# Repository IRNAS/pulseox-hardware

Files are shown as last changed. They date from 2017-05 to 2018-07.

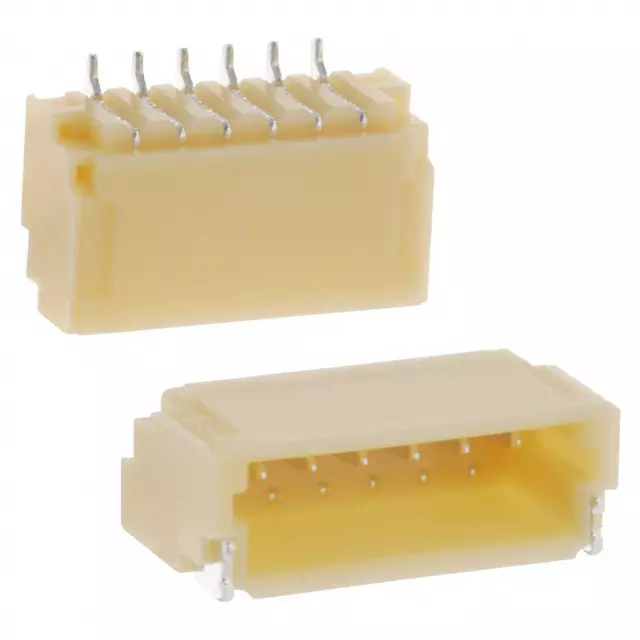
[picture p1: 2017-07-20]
Pics/JST.png

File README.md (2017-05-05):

# pulseox-hardware

---

#### License

All our projects are as usefully open-source as possible.

Hardware including documentation is licensed under [CERN OHL v.1.2. license](http://www.ohwr.org/licenses/cern-ohl/v1.2)

Firmware and software originating from the project is licensed under [GNU GENERAL PUBLIC LICENSE v3](http://www.gnu.org/licenses/gpl-3.0.en.html).

Open data generated by our projects is licensed under [CC0](https://creativecommons.org/publicdomain/zero/1.0/legalcode).

All our websites and additional documentation are licensed under [Creative Commons Attribution-ShareAlike 4 .0 Unported License] (https://creativecommons.org/licenses/by-sa/4.0/legalcode).

What this means is that you can use hardware, firmware, software and documentation without paying a royalty and knowing that you'll be able to use your version forever. You are also free to make changes but if you share these changes then you have to do so on the same conditions that you enjoy.

Koruza, GoodEnoughCNC and IRNAS are all names and marks of Institut IRNAS Rače. 
You may use these names and terms only to attribute the appropriate entity as required by the Open Licences referred to above. You may not use them in any other way and in particular you may not use them to imply endorsement or authorization of any hardware that you design, make or sell.

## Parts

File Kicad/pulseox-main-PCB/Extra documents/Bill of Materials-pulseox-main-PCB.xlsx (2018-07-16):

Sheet: Part List Report
 | Component list |  |  | GliaX - pulseox
 | Source Data From: | pulseox-main-PCB.PrjPcb |  |  | Contact:
 | Project: | pulseox-main-PCB.PrjPcb
 | Variant: | None |  |  |  |  |  |  | IRNAS
 | Report Date: | 02/24/2018 | 8:23:24 PM |  |  |  |  |  | www.irnas.eu
 | Print Date: | 2018-02-24 | 43155.84973
# | Manufacturer Part Number 1 | Manufacturer 1 | Description | Footprint | Designator | Quantity | Supplier 1 | Supplier Part Number 1 | Supplier Order Qty 1 | Supplier Stock 1 | Supplier Unit Price 1 | Supplier Subtotal 1 | Supplier Currency 1
1 | WR08X1002FTL (https://octopart-clicks.com/click/altium?manufacturer=Walsin%20Technologies&mpn=WR08X1002FTL&seller=Farnell&sku=2502671&country=US&channel=BOM%20Report) | Walsin Technologies (https://octopart-clicks.com/click/altium?manufacturer=Walsin%20Technologies&mpn=WR08X1002FTL&seller=Farnell&sku=2502671&country=US&channel=BOM%20Report) | WALSIN - WR08X1002FTL - RES, THICK FILM, 10K, 1%, 150V, 0805 | RES0805 | R4, R6 | 2 | Farnell | 2502671 (https://octopart-clicks.com/click/altium?manufacturer=Walsin%20Technologies&mpn=WR08X1002FTL&seller=Farnell&sku=2502671&country=US&channel=BOM%20Report) | 10 | 43713 | 0.05 | 0.47 | EUR
2 | CRCW08054K70FKEA (https://octopart-clicks.com/click/altium?manufacturer=Vishay&mpn=CRCW08054K70FKEA&seller=Farnell&sku=1469923&country=US&channel=BOM%20Report) | Vishay (https://octopart-clicks.com/click/altium?manufacturer=Vishay&mpn=CRCW08054K70FKEA&seller=Farnell&sku=1469923&country=US&channel=BOM%20Report) | VISHAY - CRCW08054K70FKEA - RES, THICK FILM, 4K7, 1%, 0.125W, 0805 | RES0805 | R3 | 1 | Farnell | 1469923 (https://octopart-clicks.com/click/altium?manufacturer=Vishay&mpn=CRCW08054K70FKEA&seller=Farnell&sku=1469923&country=US&channel=BOM%20Report) | 5 | 3420 |  |  | EUR
3 | WCR0805-47KFI (https://octopart-clicks.com/click/altium?manufacturer=TT%20Welwyn&mpn=WCR0805-47KFI&seller=Farnell&sku=1099812&country=US&channel=BOM%20Report) | TT Welwyn (https://octopart-clicks.com/click/altium?manufacturer=TT%20Welwyn&mpn=WCR0805-47KFI&seller=Farnell&sku=1099812&country=US&channel=BOM%20Report) | WELWYN - WCR0805-47KFI - RES, THICK FILM, 47K, 1%, 0.125W, 0805 | RES0805 | R5 | 1 | Farnell | 1099812 (https://octopart-clicks.com/click/altium?manufacturer=TT%20Welwyn&mpn=WCR0805-47KFI&seller=Farnell&sku=1099812&country=US&channel=BOM%20Report) | 5 | 16160 |  |  | EUR
4 | 1776275-2 (https://octopart-clicks.com/click/altium?manufacturer=TE%20Connectivity&mpn=1776275-2&seller=Farnell&sku=1098611&country=US&channel=BOM%20Report) | TE Connectivity (https://octopart-clicks.com/click/altium?manufacturer=TE%20Connectivity&mpn=1776275-2&seller=Farnell&sku=1098611&country=US&channel=BOM%20Report) | TE CONNECTIVITY - 1776275-2 - TERMINAL BLOCK, WIRE TO BRD, 2POS, 18AWG | Block Terminal 3.5mm | CON2 | 1 | Farnell | 1098611 (https://octopart-clicks.com/click/altium?manufacturer=TE%20Connectivity&mpn=1776275-2&seller=Farnell&sku=1098611&country=US&channel=BOM%20Report) | 5 | 28930 | 0.24 | 1.20 | EUR
5 | CGA4J1X5R1C106K125AC (https://octopart-clicks.com/click/altium?manufacturer=TDK&mpn=CGA4J1X5R1C106K125AC&seller=Farnell&sku=2210948RL&country=US&channel=BOM%20Report) | TDK (https://octopart-clicks.com/click/altium?manufacturer=TDK&mpn=CGA4J1X5R1C106K125AC&seller=Farnell&sku=2210948RL&country=US&channel=BOM%20Report) | TDK - CGA4J1X5R1C106K125AC - CAP, MLCC, X5R, 10UF, 16V, 0805 | CAP0805 | C1 | 1 | Farnell | 2210948RL (https://octopart-clicks.com/click/altium?manufacturer=TDK&mpn=CGA4J1X5R1C106K125AC&seller=Farnell&sku=2210948RL&country=US&channel=BOM%20Report) | 5 | 0 |  |  | EUR
6 | STM32F070F6P6 (https://octopart-clicks.com/click/altium?manufacturer=STMicroelectronics&mpn=STM32F070F6P6&seller=Farnell&sku=2488284&country=US&channel=BOM%20Report) | STMicroelectronics (https://octopart-clicks.com/click/altium?manufacturer=STMicroelectronics&mpn=STM32F070F6P6&seller=Farnell&sku=2488284&country=US&channel=BOM%20Report) | STMICROELECTRONICS STM32F070F6P6 32 Bit Microcontroller, Value Line, ARM Cortex-M0, 48 MHz, 32 KB, 6 KB, 20 Pins, TSSOP | SOP127P600-8N | U3 | 1 | Farnell | 2488284 (https://octopart-clicks.com/click/altium?manufacturer=STMicroelectronics&mpn=STM32F070F6P6&seller=Farnell&sku=2488284&country=US&channel=BOM%20Report) | 5 | 6081 | 2.11 | 10.55 | EUR
7 | AT-2440-TWT-R (https://octopart-clicks.com/click/altium?manufacturer=Projects%20Unlimited&mpn=AT-2440-TWT-R&seller=Digi-Key&sku=668-1103-ND&country=US&channel=BOM%20Report) | Projects Unlimited (https://octopart-clicks.com/click/altium?manufacturer=Projects%20Unlimited&mpn=AT-2440-TWT-R&seller=Digi-Key&sku=668-1103-ND&country=US&channel=BOM%20Report) | AUDIO PIEZO TRANSDUCER 1-30V TH | Buzzer | BUZ1 | 1 | Digi-Key | 668-1103-ND (https://octopart-clicks.com/click/altium?manufacturer=Projects%20Unlimited&mpn=AT-2440-TWT-R&seller=Digi-Key&sku=668-1103-ND&country=US&channel=BOM%20Report) | 5 | 3084 | 1.87 | 9.35 | USD
8 | PS000036 (https://octopart-clicks.com/click/altium?manufacturer=Pro%20Signal&mpn=PS000036&seller=Farnell&sku=2787075&country=US&channel=BOM%20Report) | Pro Signal (https://octopart-clicks.com/click/altium?manufacturer=Pro%20Signal&mpn=PS000036&seller=Farnell&sku=2787075&country=US&channel=BOM%20Report) |  | eth con | CON3 | 1 | Farnell | 2787075 (https://octopart-clicks.com/click/altium?manufacturer=Pro%20Signal&mpn=PS000036&seller=Farnell&sku=2787075&country=US&channel=BOM%20Report) |  | 0 |  |  | Loading...
9 | NX7002BK (https://octopart-clicks.com/click/altium?manufacturer=NXP%20Semiconductors&mpn=NX7002BK&seller=Farnell&sku=2469640&country=US&channel=BOM%20Report) | NXP Semiconductors (https://octopart-clicks.com/click/altium?manufacturer=NXP%20Semiconductors&mpn=NX7002BK&seller=Farnell&sku=2469640&country=US&channel=BOM%20Report) | NEXPERIA - NX7002BK - MOSFET, N-CH, 60V, 0.27A, SOT-23-3 | SOT23 | T1 | 1 | Farnell | 2469640 (https://octopart-clicks.com/click/altium?manufacturer=NXP%20Semiconductors&mpn=NX7002BK&seller=Farnell&sku=2469640&country=US&channel=BOM%20Report) | 5 | 175 | 0.26 | 1.29 | EUR
10 | GRM219R71C104KA01D (https://octopart-clicks.com/click/altium?manufacturer=Murata&mpn=GRM219R71C104KA01D&seller=Farnell&sku=2611934&country=US&channel=BOM%20Report) | Murata (https://octopart-clicks.com/click/altium?manufacturer=Murata&mpn=GRM219R71C104KA01D&seller=Farnell&sku=2611934&country=US&channel=BOM%20Report) | MURATA - GRM219R71C104KA01D - CAP, MLCC, X7R, 0.1UF, 16V, 0805 | CAP0805 | C2, C16 | 2 | Farnell | 2611934 (https://octopart-clicks.com/click/altium?manufacturer=Murata&mpn=GRM219R71C104KA01D&seller=Farnell&sku=2611934&country=US&channel=BOM%20Report) | 10 | 4457 | 0.10 | 0.98 | EUR
11 | GRM21BR71C105KA01K (https://octopart-clicks.com/click/altium?manufacturer=Murata&mpn=GRM21BR71C105KA01K&seller=Farnell&sku=2688536&country=US&channel=BOM%20Report) | Murata (https://octopart-clicks.com/click/altium?manufacturer=Murata&mpn=GRM21BR71C105KA01K&seller=Farnell&sku=2688536&country=US&channel=BOM%20Report) | MURATA - GRM21BR71C105KA01K - CAP, MLCC, X7R, 1UF, 16V, 0805 | CAP0805 | C3, C4 | 2 | Farnell | 2688536 (https://octopart-clicks.com/click/altium?manufacturer=Murata&mpn=GRM21BR71C105KA01K&seller=Farnell&sku=2688536&country=US&channel=BOM%20Report) | 10 | 15026 | 0.10 | 1.03 | EUR
12 | MCWR08X1002FTL (https://octopart-clicks.com/click/altium?manufacturer=Multicomp&mpn=MCWR08X1002FTL&seller=Farnell&sku=2446870&country=US&channel=BOM%20Report) | Multicomp (https://octopart-clicks.com/click/altium?manufacturer=Multicomp&mpn=MCWR08X1002FTL&seller=Farnell&sku=2446870&country=US&channel=BOM%20Report) | MULTICOMP MCWR08X1002FTL Surface Mount Chip Resistor, Thick Film, MCWR Series, 10 kohm, 125 mW, 1%, 150 V | RES0805 | R7 | 1 | Farnell | 2446870 (https://octopart-clicks.com/click/altium?manufacturer=Multicomp&mpn=MCWR08X1002FTL&seller=Farnell&sku=2446870&country=US&channel=BOM%20Report) | 5 | 2650000 |  |  | EUR
13 | MCMR06X102JTL (https://octopart-clicks.com/click/altium?manufacturer=Multicomp&mpn=MCMR06X102JTL&seller=Farnell&sku=2073354&country=US&channel=BOM%20Report) | Multicomp (https://octopart-clicks.com/click/altium?manufacturer=Multicomp&mpn=MCMR06X102JTL&seller=Farnell&sku=2073354&country=US&channel=BOM%20Report) | MULTICOMP - MCMR06X102 JTL - RES, CERAMIC, 1K, 5%, 0.1W, 0603 | RES0603 | R2 | 1 | Farnell | 2073354 (https://octopart-clicks.com/click/altium?manufacturer=Multicomp&mpn=MCMR06X102JTL&seller=Farnell&sku=2073354&country=US&channel=BOM%20Report) | 5 | 11690 |  |  | EUR
14 | MCMR06X103JTL (https://octopart-clicks.com/click/altium?manufacturer=Multicomp&mpn=MCMR06X103JTL&seller=Farnell&sku=2073356&country=US&channel=BOM%20Report) | Multicomp (https://octopart-clicks.com/click/altium?manufacturer=Multicomp&mpn=MCMR06X103JTL&seller=Farnell&sku=2073356&country=US&channel=BOM%20Report) | MULTICOMP - MCMR06X103 JTL - RES, CERAMIC, 10K, 5%, 0.1W, 0603 | RES0603 | R1 | 1 | Farnell | 2073356 (https://octopart-clicks.com/click/altium?manufacturer=Multicomp&mpn=MCMR06X103JTL&seller=Farnell&sku=2073356&country=US&channel=BOM%20Report) | 5 | 11369 |  |  | EUR
15 | MCP1700T-3002E/TT (https://octopart-clicks.com/click/altium?manufacturer=Microchip&mpn=MCP1700T-3002E%2FTT&seller=Farnell&sku=1331482&country=US&channel=BOM%20Report) | Microchip (https://octopart-clicks.com/click/altium?manufacturer=Microchip&mpn=MCP1700T-3002E%2FTT&seller=Farnell&sku=1331482&country=US&channel=BOM%20Report) | MICROCHIP - MCP1700T-3002E/TT - IC, LDO REGULATOR, 0.25A, 6V, SOT23-3 | SOT23127P600-8N - duplicate | U2 | 1 | Farnell | 1331482 (https://octopart-clicks.com/click/altium?manufacturer=Microchip&mpn=MCP1700T-3002E%2FTT&seller=Farnell&sku=1331482&country=US&channel=BOM%20Report) | 5 | 25139 | 0.34 | 1.70 | EUR
16 | MCP73831T-2ACI/OT (https://octopart-clicks.com/click/altium?manufacturer=Microchip&mpn=MCP73831T-2ACI%2FOT&seller=Farnell&sku=1332158&country=US&channel=BOM%20Report) | Microchip (https://octopart-clicks.com/click/altium?manufacturer=Microchip&mpn=MCP73831T-2ACI%2FOT&seller=Farnell&sku=1332158&country=US&channel=BOM%20Report) | MICROCHIP - MCP73831T-2ACI/OT - LI-ION/LI-POLY CHARGE CONTROLLER | SOT23127P600-8N | U1 | 1 | Farnell | 1332158 (https://octopart-clicks.com/click/altium?manufacturer=Microchip&mpn=MCP73831T-2ACI%2FOT&seller=Farnell&sku=1332158&country=US&channel=BOM%20Report) | 5 | 41449 | 0.52 | 2.60 | EUR
17 | Loading... (https://octopart-clicks.com/click/altium?manufacturer=Loading...&mpn=Loading...&seller=Farnell&sku=1813692&country=US&channel=BOM%20Report) | Loading... (https://octopart-clicks.com/click/altium?manufacturer=Loading...&mpn=Loading...&seller=Farnell&sku=1813692&country=US&channel=BOM%20Report) | TE CONNECTIVITY FSMRA4JH04 Tactile Switch, Non Illuminated, 1.57 N, 24 V, 50 mA, Solder, FSMRAJ Series | SW TH ANGLE_1 | SW4 | 1 | Farnell | 1813692 (https://octopart-clicks.com/click/altium?manufacturer=Loading...&mpn=Loading...&seller=Farnell&sku=1813692&country=US&channel=BOM%20Report) |  |  |  |  | Loading...
18 | OS102011MA1QS1 (https://octopart-clicks.com/click/altium?manufacturer=ITT%20C%26K&mpn=OS102011MA1QS1&seller=Farnell&sku=2435103&country=US&channel=BOM%20Report) | ITT C&K (https://octopart-clicks.com/click/altium?manufacturer=ITT%20C%26K&mpn=OS102011MA1QS1&seller=Farnell&sku=2435103&country=US&channel=BOM%20Report) | C & K COMPONENTS - OS102011MA1QS1 - SWITCH SLIDE SHORTING SPDT | SLIDE_SW | SW1 | 1 | Farnell | 2435103 (https://octopart-clicks.com/click/altium?manufacturer=ITT%20C%26K&mpn=OS102011MA1QS1&seller=Farnell&sku=2435103&country=US&channel=BOM%20Report) | 5 | 1441 | 0.25 | 1.25 | EUR
19 | PTS645VH58-2LFS (https://octopart-clicks.com/click/altium?manufacturer=ITT%20C%26K&mpn=PTS645VH58-2LFS&seller=Farnell&sku=2320088&country=US&channel=BOM%20Report) | ITT C&K (https://octopart-clicks.com/click/altium?manufacturer=ITT%20C%26K&mpn=PTS645VH58-2LFS&seller=Farnell&sku=2320088&country=US&channel=BOM%20Report) | SWITCH TACTILE SPST-NO 0.05A 12V | SW TH ANGLE_2 | SW2 | 1 | Farnell | 2320088 (https://octopart-clicks.com/click/altium?manufacturer=ITT%20C%26K&mpn=PTS645VH58-2LFS&seller=Farnell&sku=2320088&country=US&channel=BOM%20Report) | 5 | 7080 | 0.19 | 0.94 | GBP
20 | HSMS-C190 (https://octopart-clicks.com/click/altium?manufacturer=Broadcom%20Avago&mpn=HSMS-C190&seller=Farnell&sku=2497356&country=US&channel=BOM%20Report) | Broadcom Avago (https://octopart-clicks.com/click/altium?manufacturer=Broadcom%20Avago&mpn=HSMS-C190&seller=Farnell&sku=2497356&country=US&channel=BOM%20Report) | BROADCOM LIMITED - HSMS-C190 - LED, RED, 10MCD, 626NM | LED0603 | D1 | 1 | Farnell | 2497356 (https://octopart-clicks.com/click/altium?manufacturer=Broadcom%20Avago&mpn=HSMS-C190&seller=Farnell&sku=2497356&country=US&channel=BOM%20Report) |  | 11495 |  |  | Loading...
21 |  |  |  | microUSB-CHINA | CON1 | 1
22 |  |  | Header, 4-Pin | HDR1X4 | P1 | 1
23 |  |  | Header, 8-Pin | HDR1X8 | P2 | 1
 |  |  |  |  |  | 26 |  |  | 100 |  |  | 31.366
Approved |  |  |  | Notes
 |  |  |  | pcs: |  | 5 |  | Total |  | 31.366 |  | <none>
 |  |  |  |  |  |  |  | Price for 1pcs |  | 6.27 |  | <none>

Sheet: Project Information
Project Full Path | C:\Users\vojislav\Documents\Projects\pulseox-hardware\pulseox-main-PCB\pulseox-main-PCB.PrjPcb
Project Filename | pulseox-main-PCB.PrjPcb
Variant Name | None
Data-Source Filename | pulseox-main-PCB.PrjPcb
Data-Source Full Path | C:\Users\vojislav\Documents\Projects\pulseox-hardware\pulseox-main-PCB\pulseox-main-PCB.PrjPcb
Title | <Parameter Title not found>
Total Quantity | 26
Report Time | 8:23:24 PM
Report Date | 02/24/2018
Report Date & Tine | 02/24/2018 8:23:24 PM
Output Name | Bill of Materials
Output Type | BOM_PartType
Output Generator Name | BOM
Output Generator Description | Bill of Materials

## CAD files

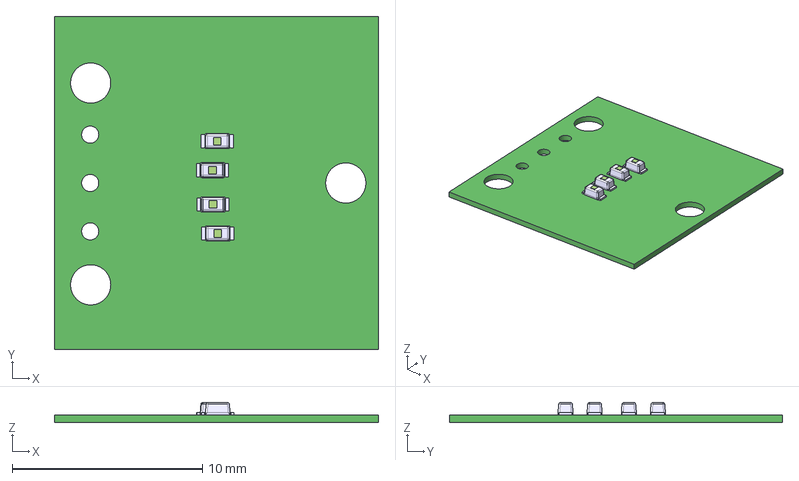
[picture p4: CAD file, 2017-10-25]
PCB_step_files/pulseox-clamp-PCB_diode_v2_0.step
17.0 x 17.5 x 1.07 mm
Board
LED_SMD_0603 x 4
Extruded x 4

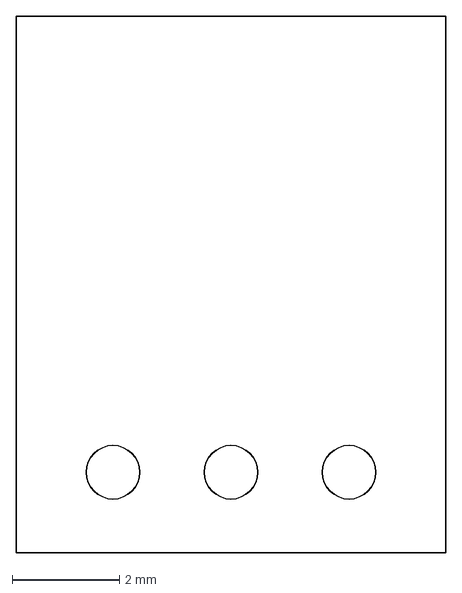
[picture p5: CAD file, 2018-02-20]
pulseox-clamp-led-PCB/pcb_test.dxf
8.00 x 10.0 mm

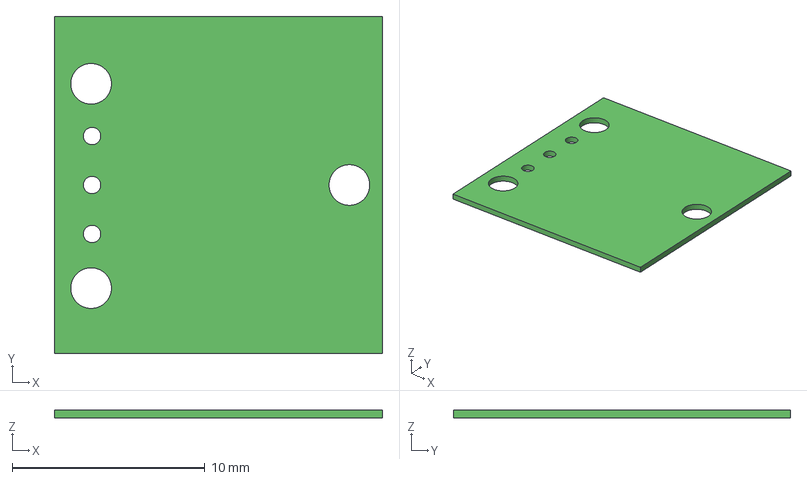
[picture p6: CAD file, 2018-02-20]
pulseox-clamp-PCB/pulseox-clamp-PCB_v2_0.step
17.0 x 17.5 x 0.411 mm

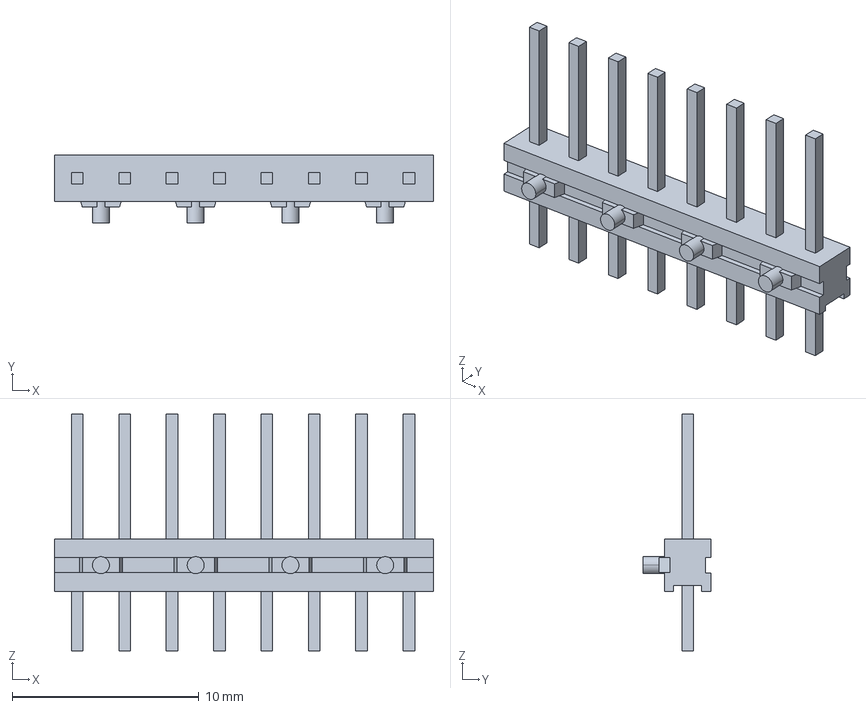
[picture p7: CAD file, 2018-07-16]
pulseox-main-PCB/step/header8pin.stp
20.3 x 3.65 x 12.7 mm

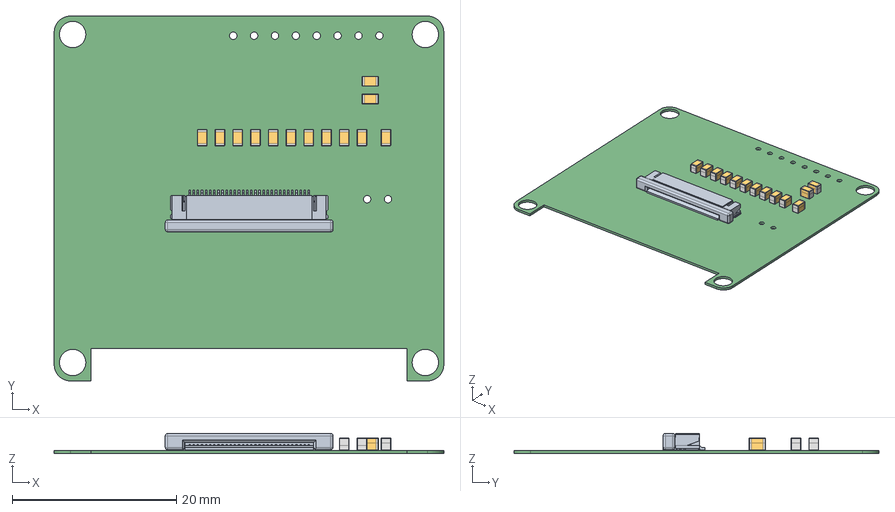
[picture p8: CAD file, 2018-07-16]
pulseox_brakeout_LCD_PCB/pulseox_brakeout_LCD_PCB.step
47.4 x 44.4 x 2.47 mm
Board
c-3-1734592-0-c-3d
CAPC2012X95N_EIA_0805 x 26

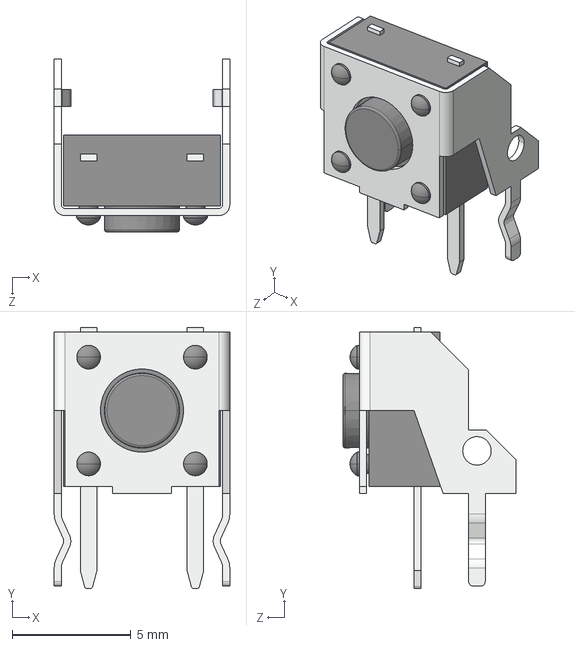
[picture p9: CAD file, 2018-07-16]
pulseox-main-PCB/step/User Library-SWITCH, TACTILE, RIGHT ANGLE, 12VDC, 50MA, 3_15MM ACTUATOR, WEALTH METAL TC-0240Z.step
7.40 x 11.0 x 7.30 mm

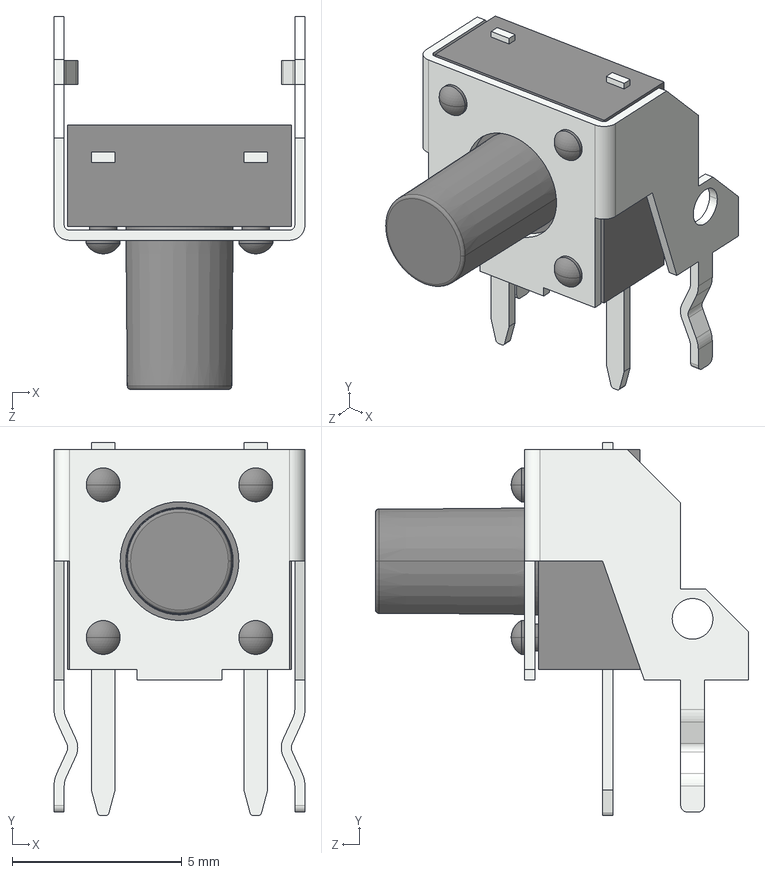
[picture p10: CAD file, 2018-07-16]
pulseox-main-PCB/step/User Library-SWITCH, TACTILE, RIGHT ANGLE, 12VDC, 50MA, 6_85MM ACTUATOR, WEALTH METAL TC-0244Z.step
7.40 x 11.0 x 11.0 mm

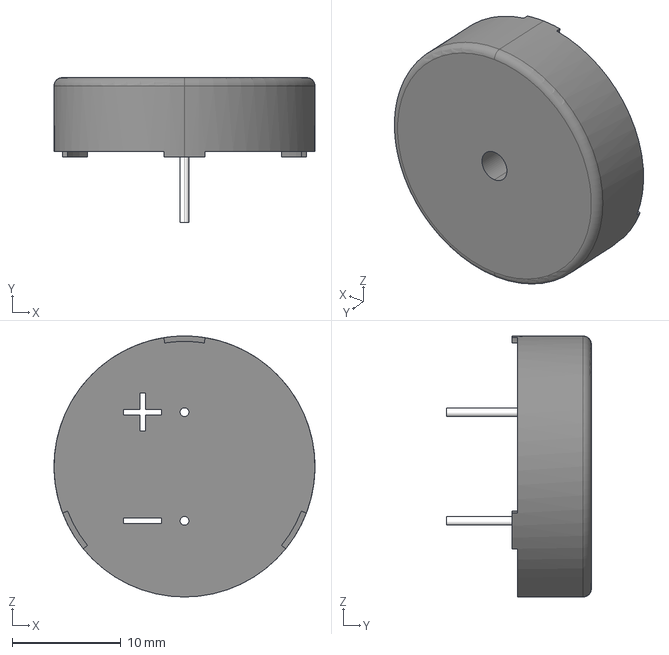
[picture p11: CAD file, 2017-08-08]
pulseox-main-PCB/step/buzz.stp
24.0 x 13.3 x 24.0 mm

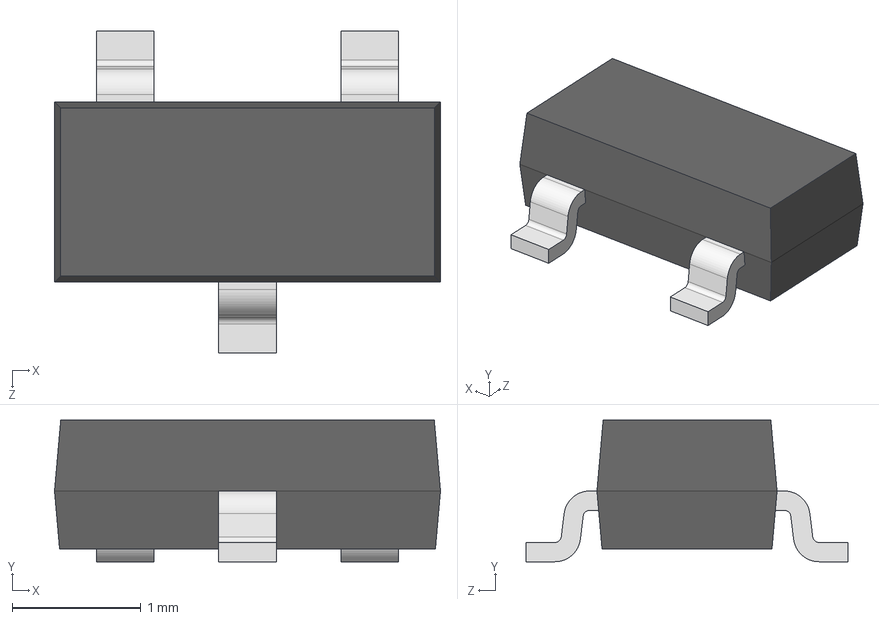
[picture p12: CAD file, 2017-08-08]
pulseox-main-PCB/step/SOT-23.step
3.00 x 1.10 x 2.50 mm

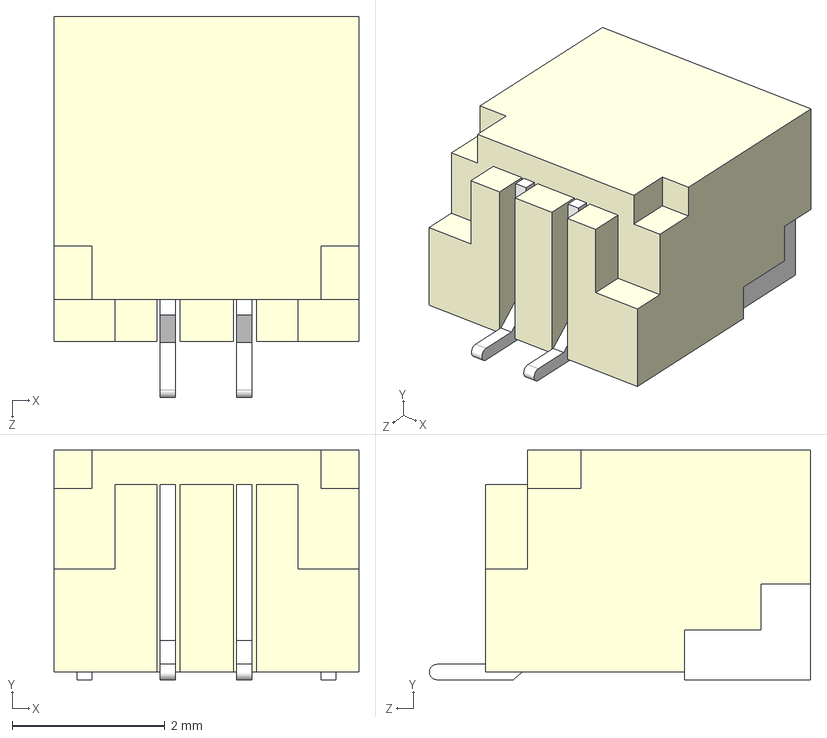
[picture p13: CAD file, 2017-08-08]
pulseox-main-PCB/step/JST_SM02B-SRSS-TB.step
3.99 x 3.00 x 4.99 mm

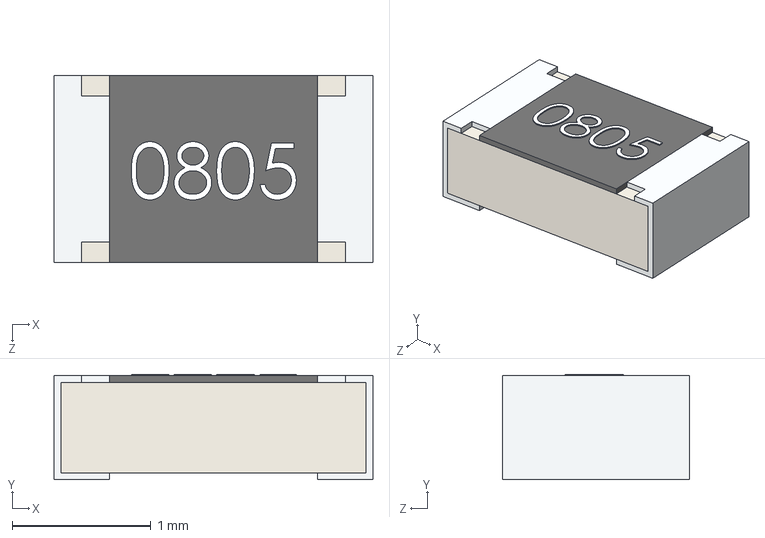
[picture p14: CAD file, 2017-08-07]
pulseox-main-PCB/step/RES-0805.step
2.30 x 0.76 x 1.35 mm

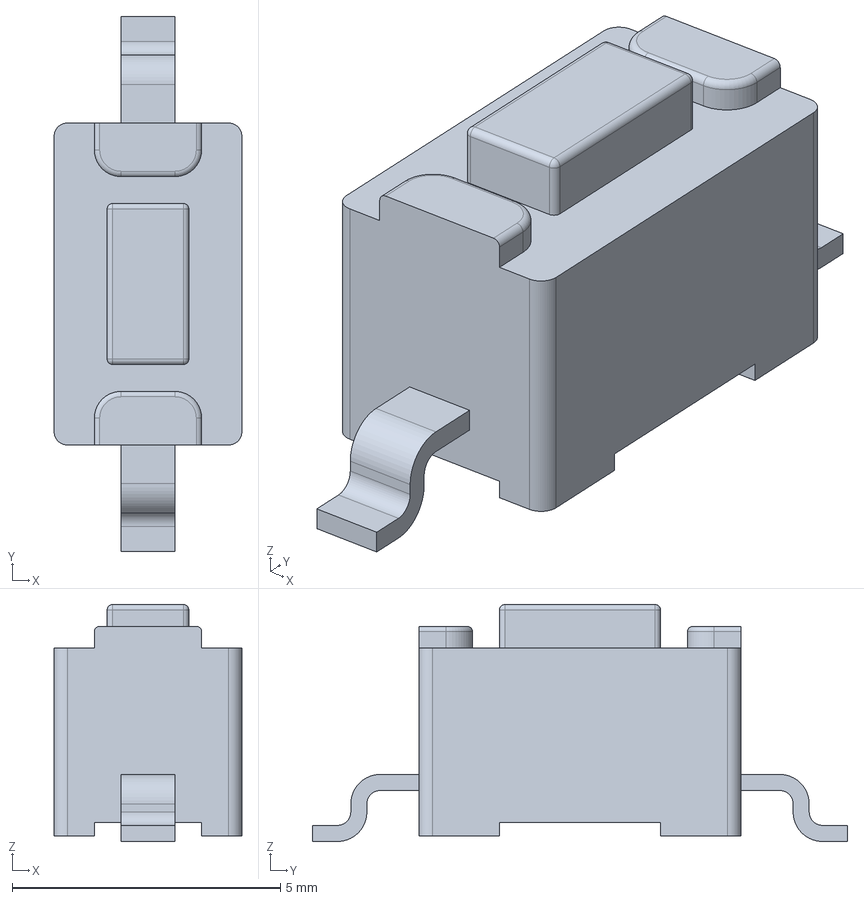
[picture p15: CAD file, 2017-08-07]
pulseox-main-PCB/step/fsmsm.stp
3.50 x 9.97 x 4.42 mm

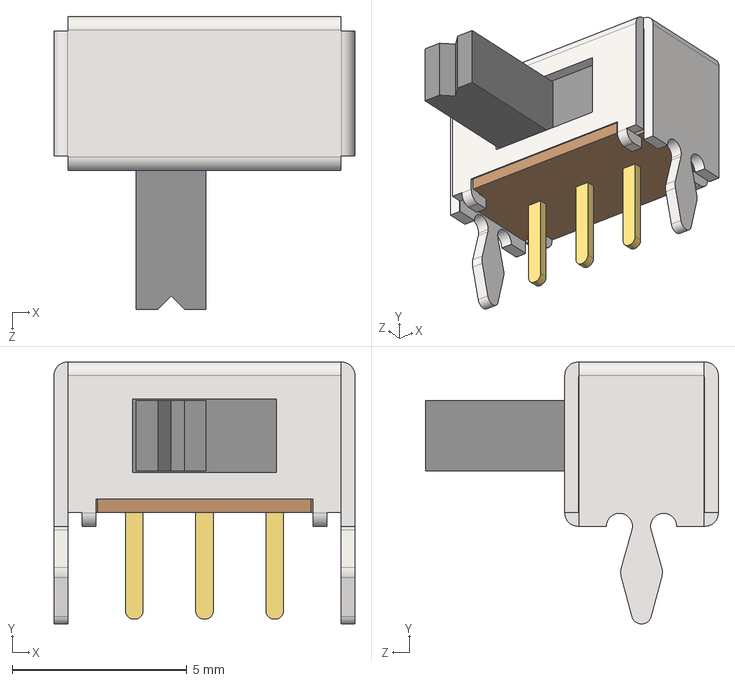
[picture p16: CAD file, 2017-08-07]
pulseox-main-PCB/step/CK_Slide.step
8.61 x 7.49 x 8.37 mm

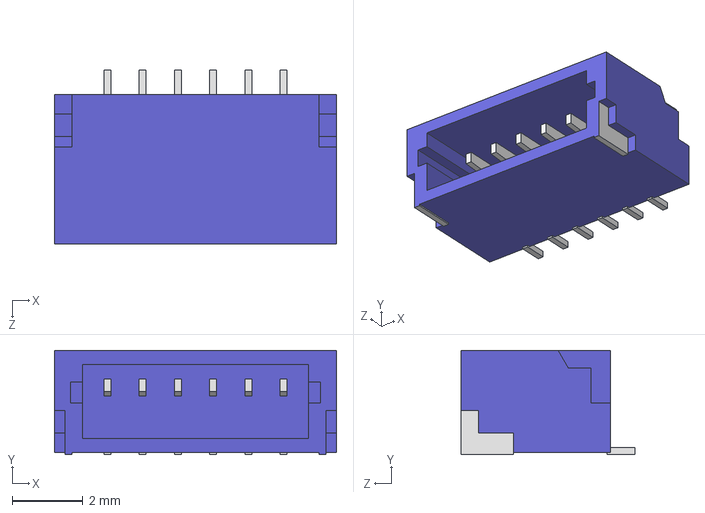
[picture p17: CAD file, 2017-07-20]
pulseox-main-PCB/step/SM06B-SRSS-TB.STEP
8.00 x 2.96 x 4.95 mm

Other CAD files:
PCB_step_files/pulseox-clamp-PCB_v2_0.step
pulseox-clamp-led-PCB/pulseox-clamp-PCB_diode_v2_0.step
pulseox-main-PCB/step/SHR-06V-S-B.STEP
pulseox-main-PCB/step/SHR-06V-S.STEP

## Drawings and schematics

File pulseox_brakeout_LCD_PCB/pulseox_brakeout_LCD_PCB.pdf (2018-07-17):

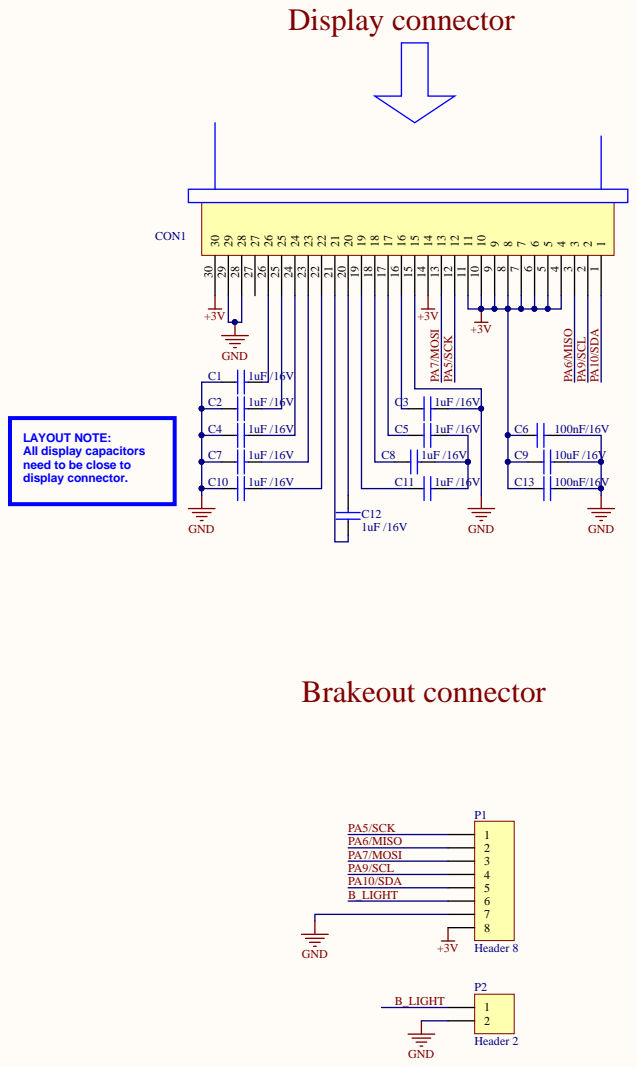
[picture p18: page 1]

LAYOUT NOTE:
All display capacitors
need to be close to
display connector.

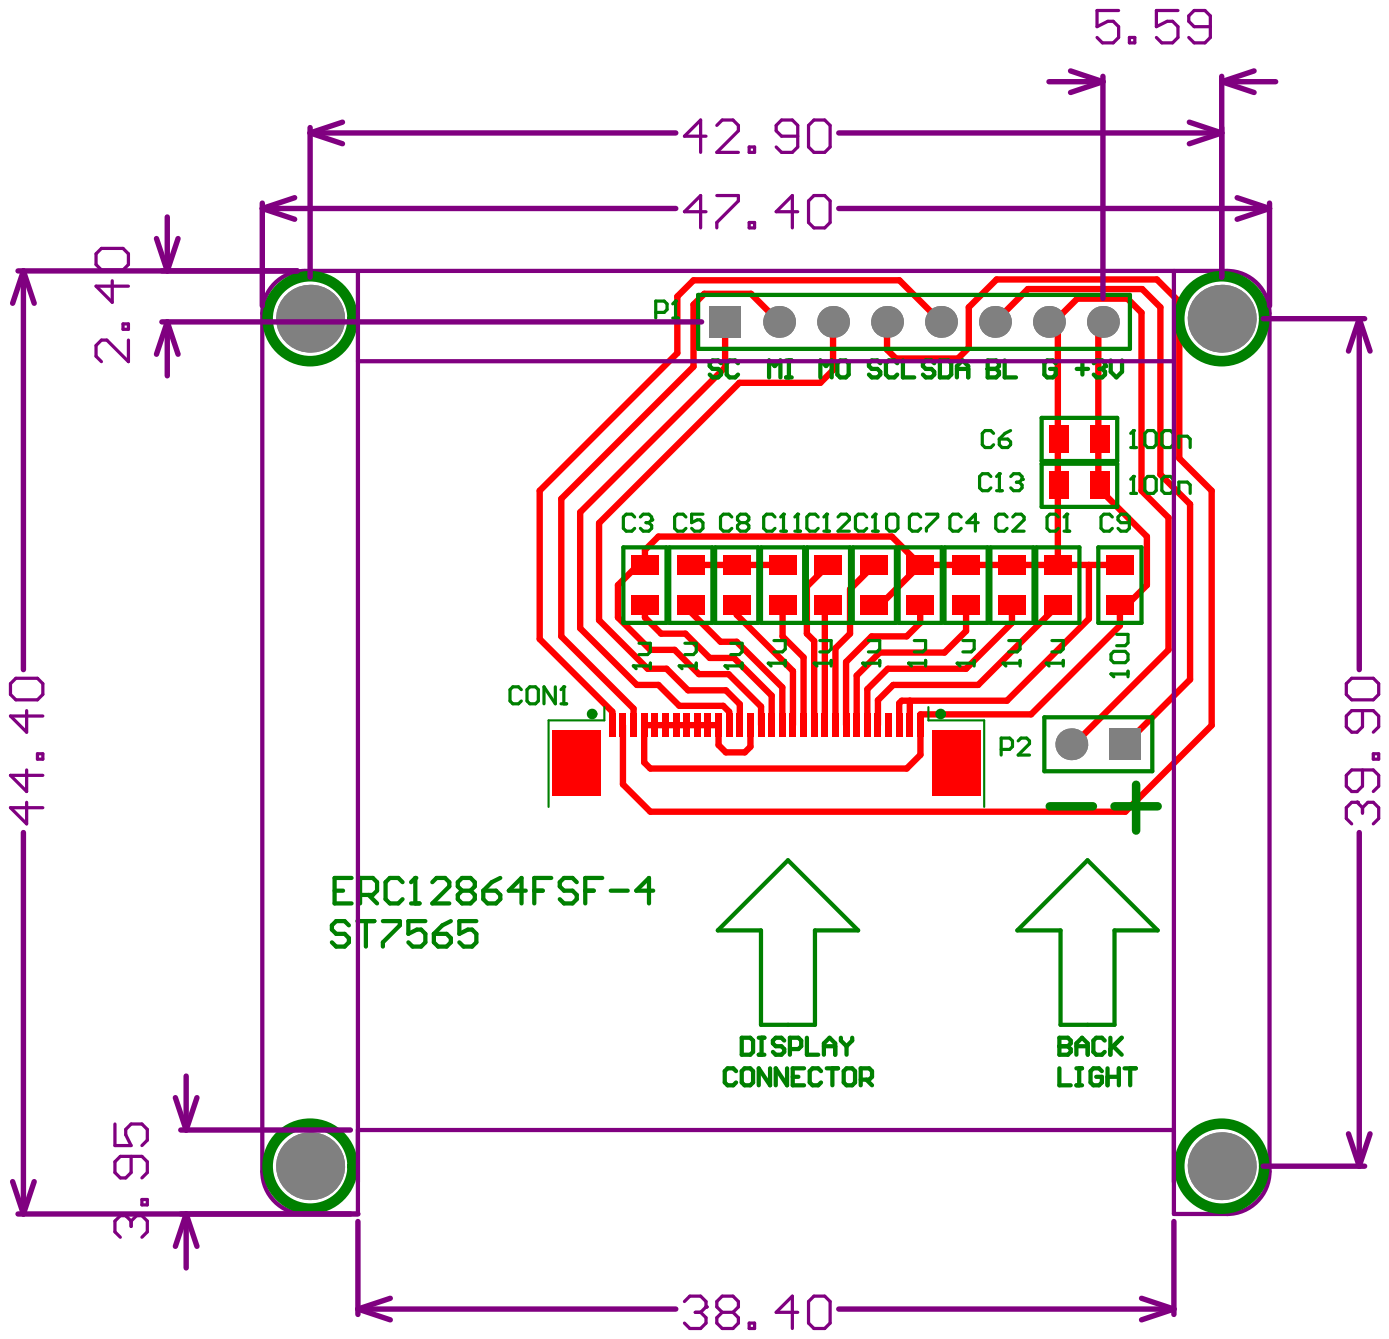
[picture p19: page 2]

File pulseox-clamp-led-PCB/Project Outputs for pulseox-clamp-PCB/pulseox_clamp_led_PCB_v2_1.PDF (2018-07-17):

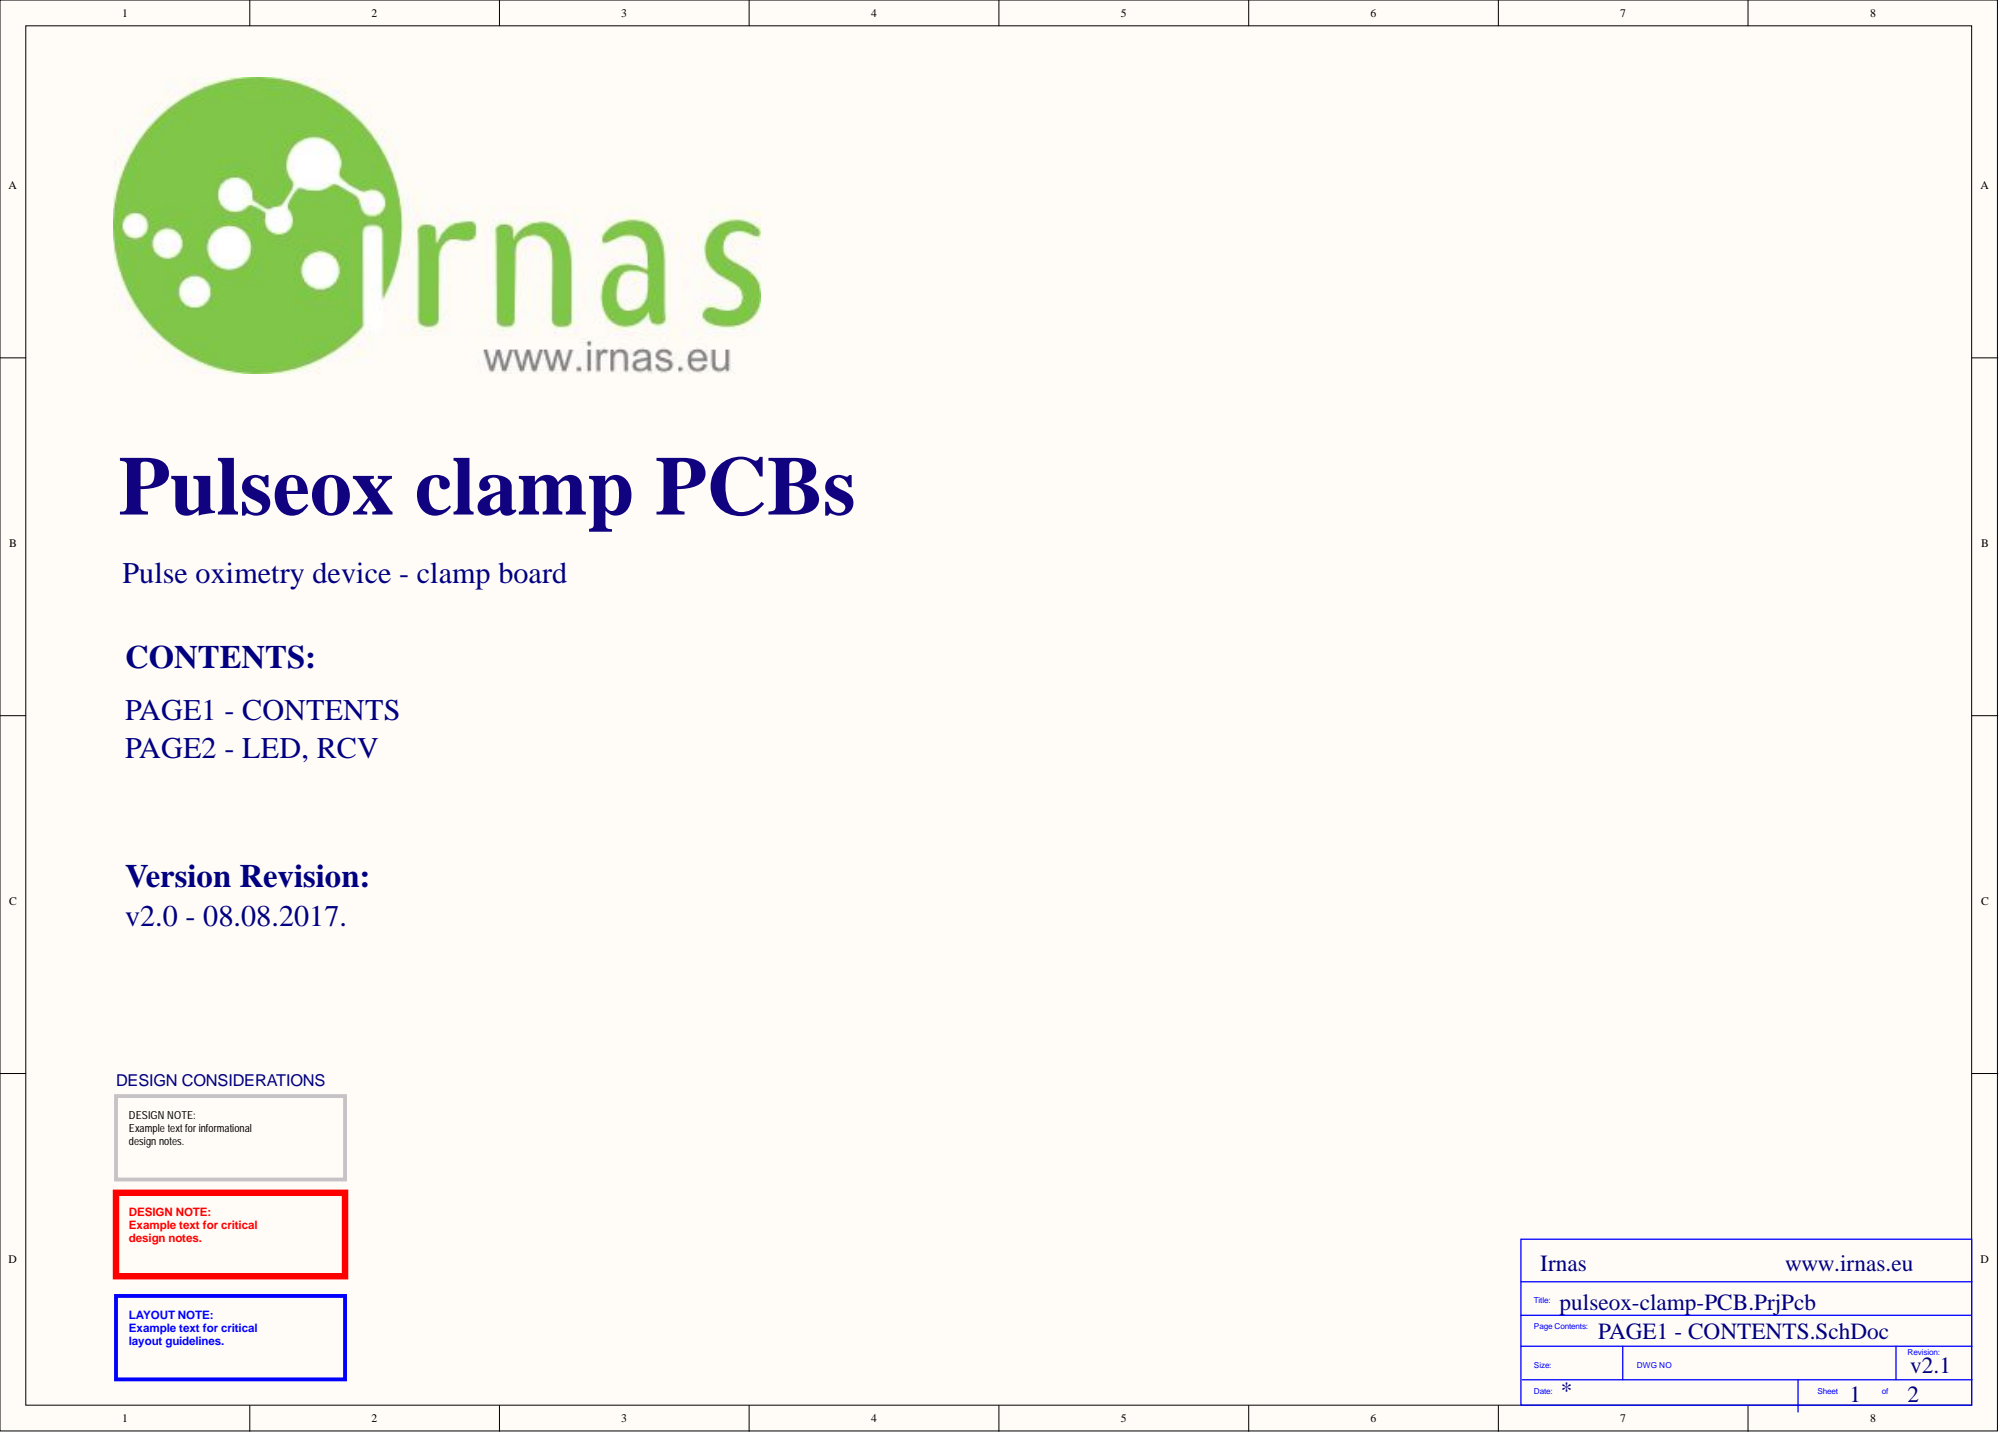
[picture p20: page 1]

Pulse oximetry device - clamp board

DESIGN NOTE:
Example text for informational
design notes.

Example text for critical

pulseox-clamp-PCB.PrjPcb
PAGE1 - CONTENTS.SchDoc

LAYOUT NOTE:
layout guidelines.

Size: | DWG NO | Revision: v2.1

* Date: | 1 2 Sheet of

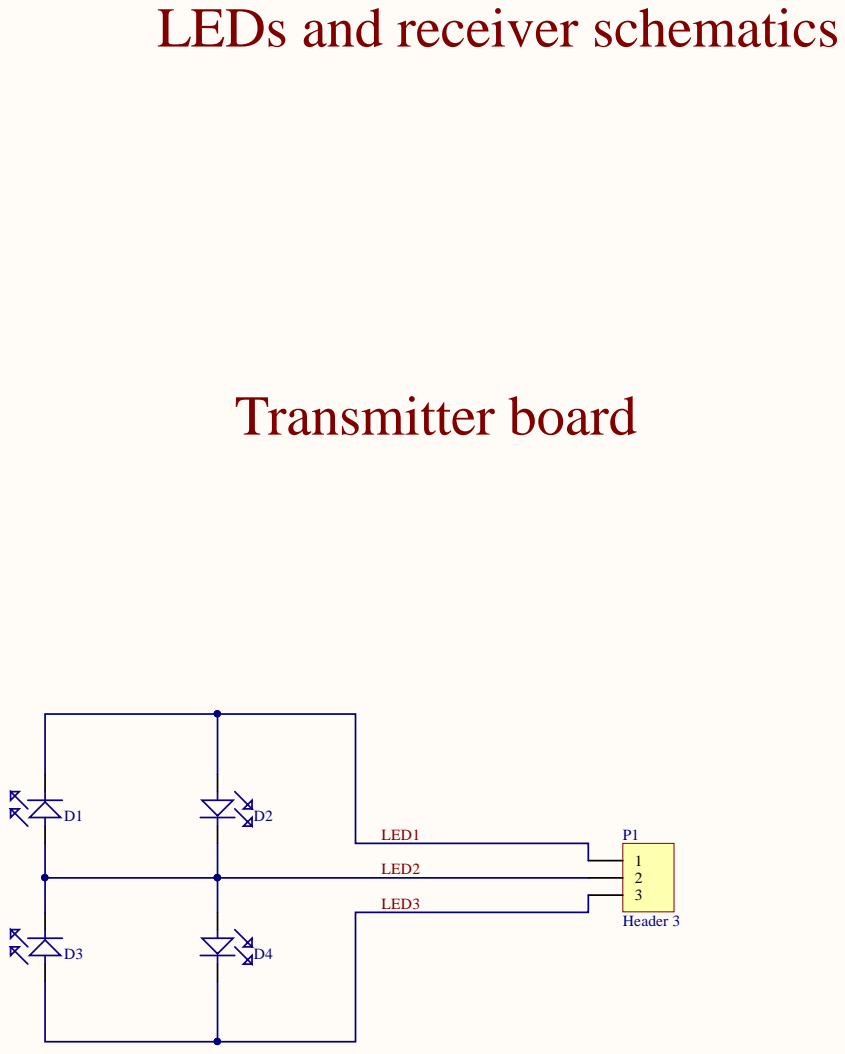
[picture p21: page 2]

LEDs and receiver schematics Transmitter board123

S i z e : | DWG N O | R e v i s i o n : v2.1

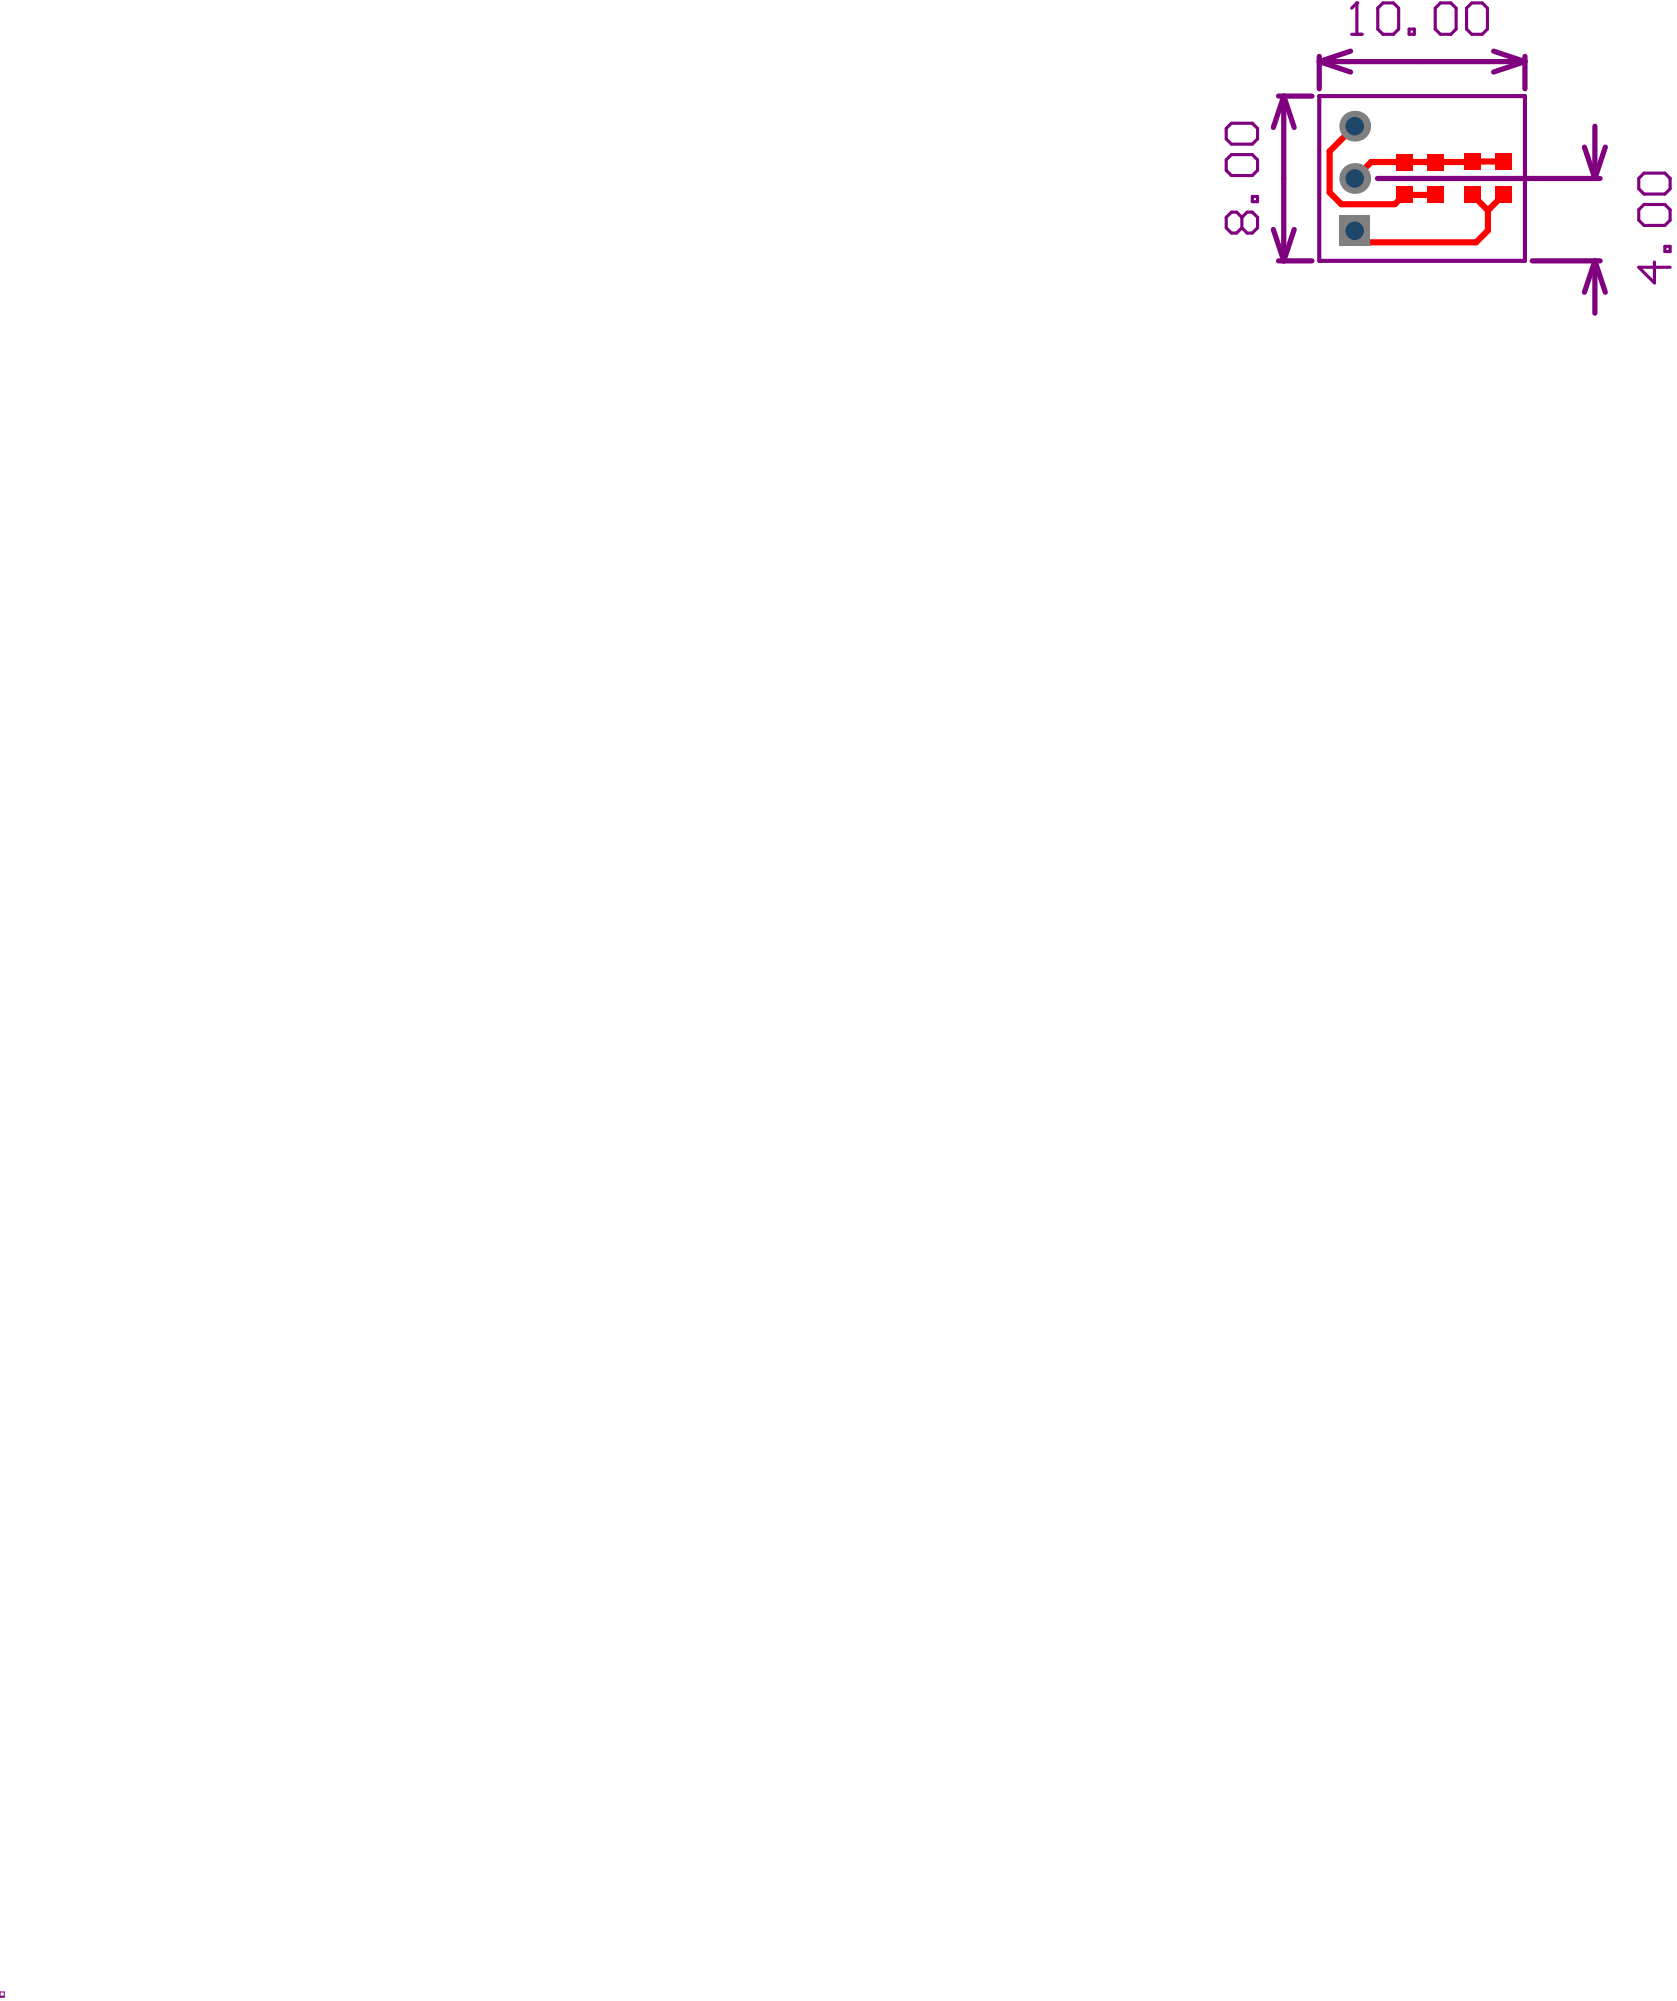
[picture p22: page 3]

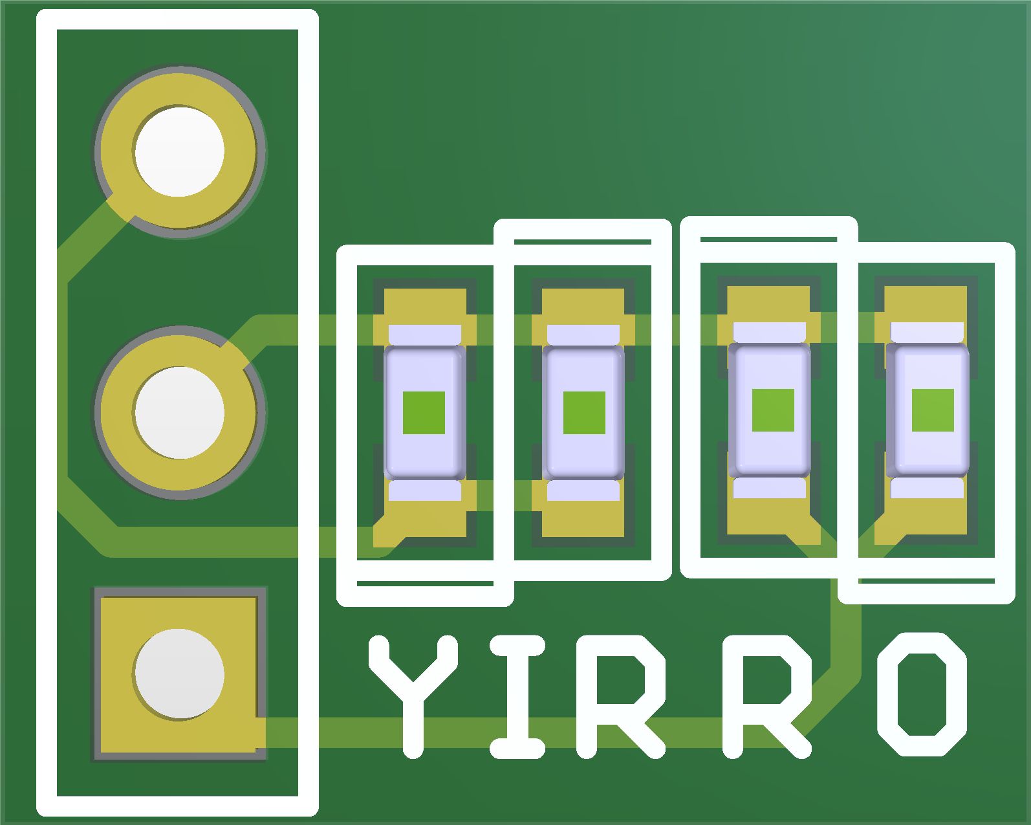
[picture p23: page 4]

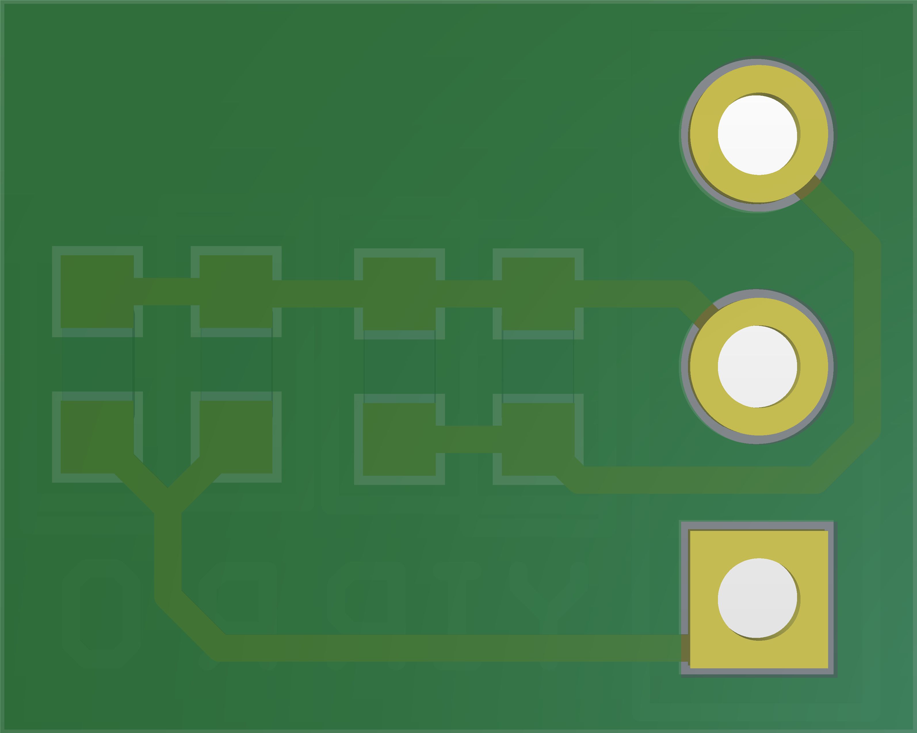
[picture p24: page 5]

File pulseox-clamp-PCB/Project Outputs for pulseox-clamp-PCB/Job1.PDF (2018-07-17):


Pulse oximetry device - clamp board

DESIGN NOTE:
Example text for informational
design notes.

Example text for critical

pulseox-clamp-PCB.PrjPcb
PAGE1 - CONTENTS.SchDoc

LAYOUT NOTE:
layout guidelines.

Size: | DWG NO | Revision: v2.1

* Date: | 1 2 Sheet of

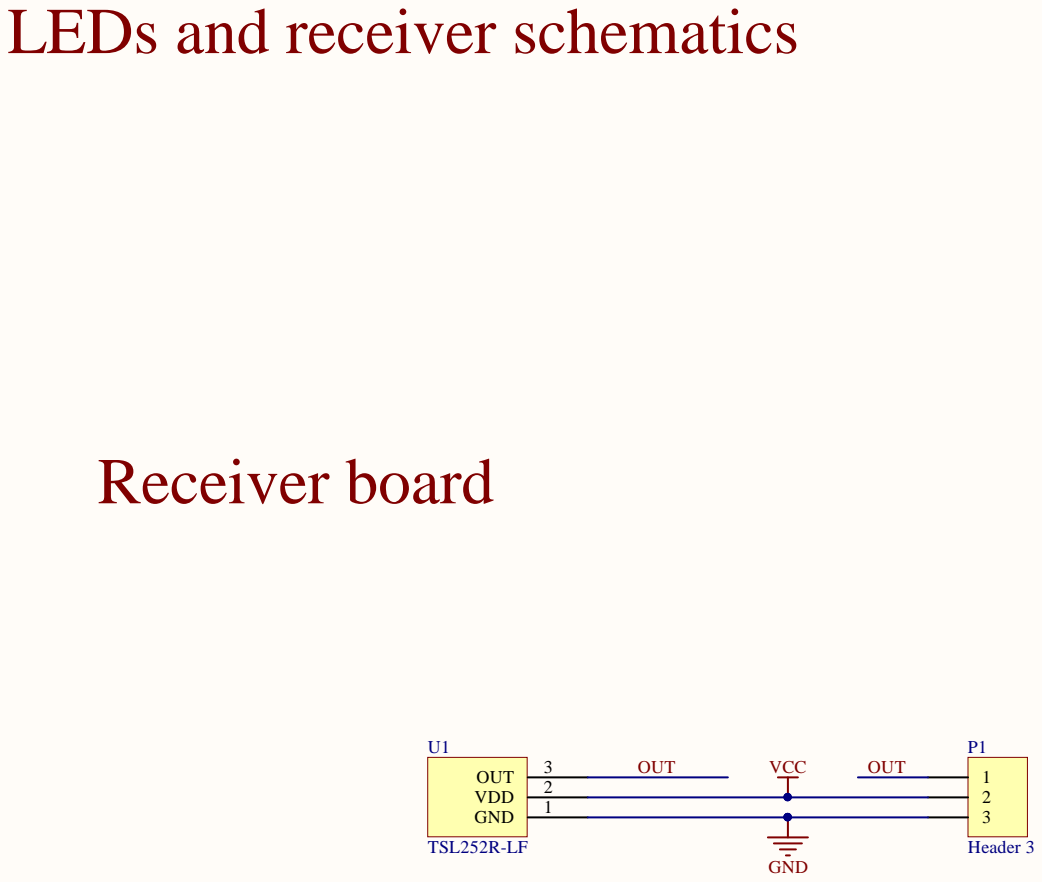
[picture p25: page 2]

LEDs and receiver schematics

S i z e : | DWG N O | R e v i s i o n : v2.1

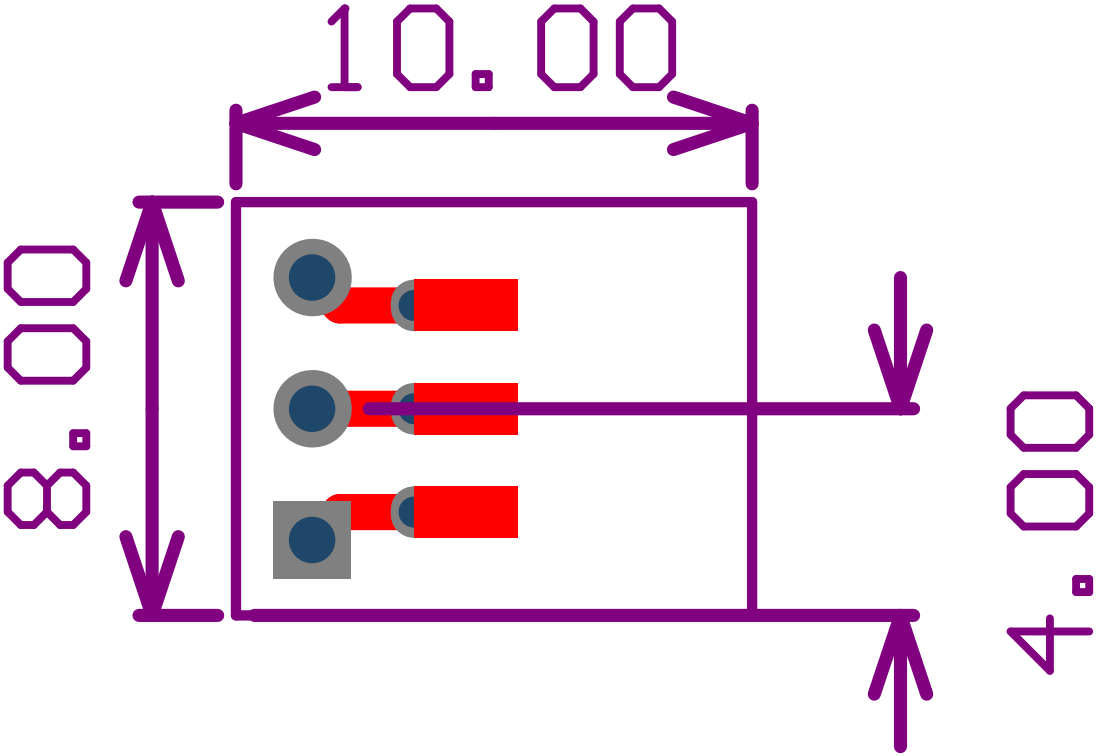
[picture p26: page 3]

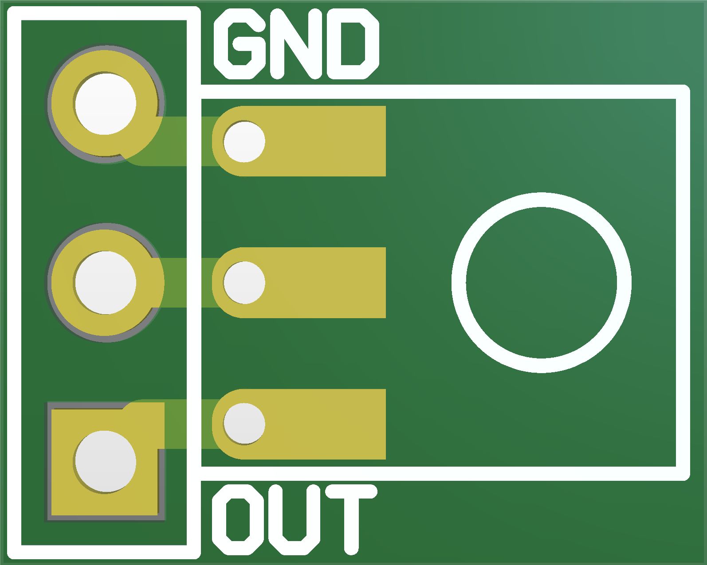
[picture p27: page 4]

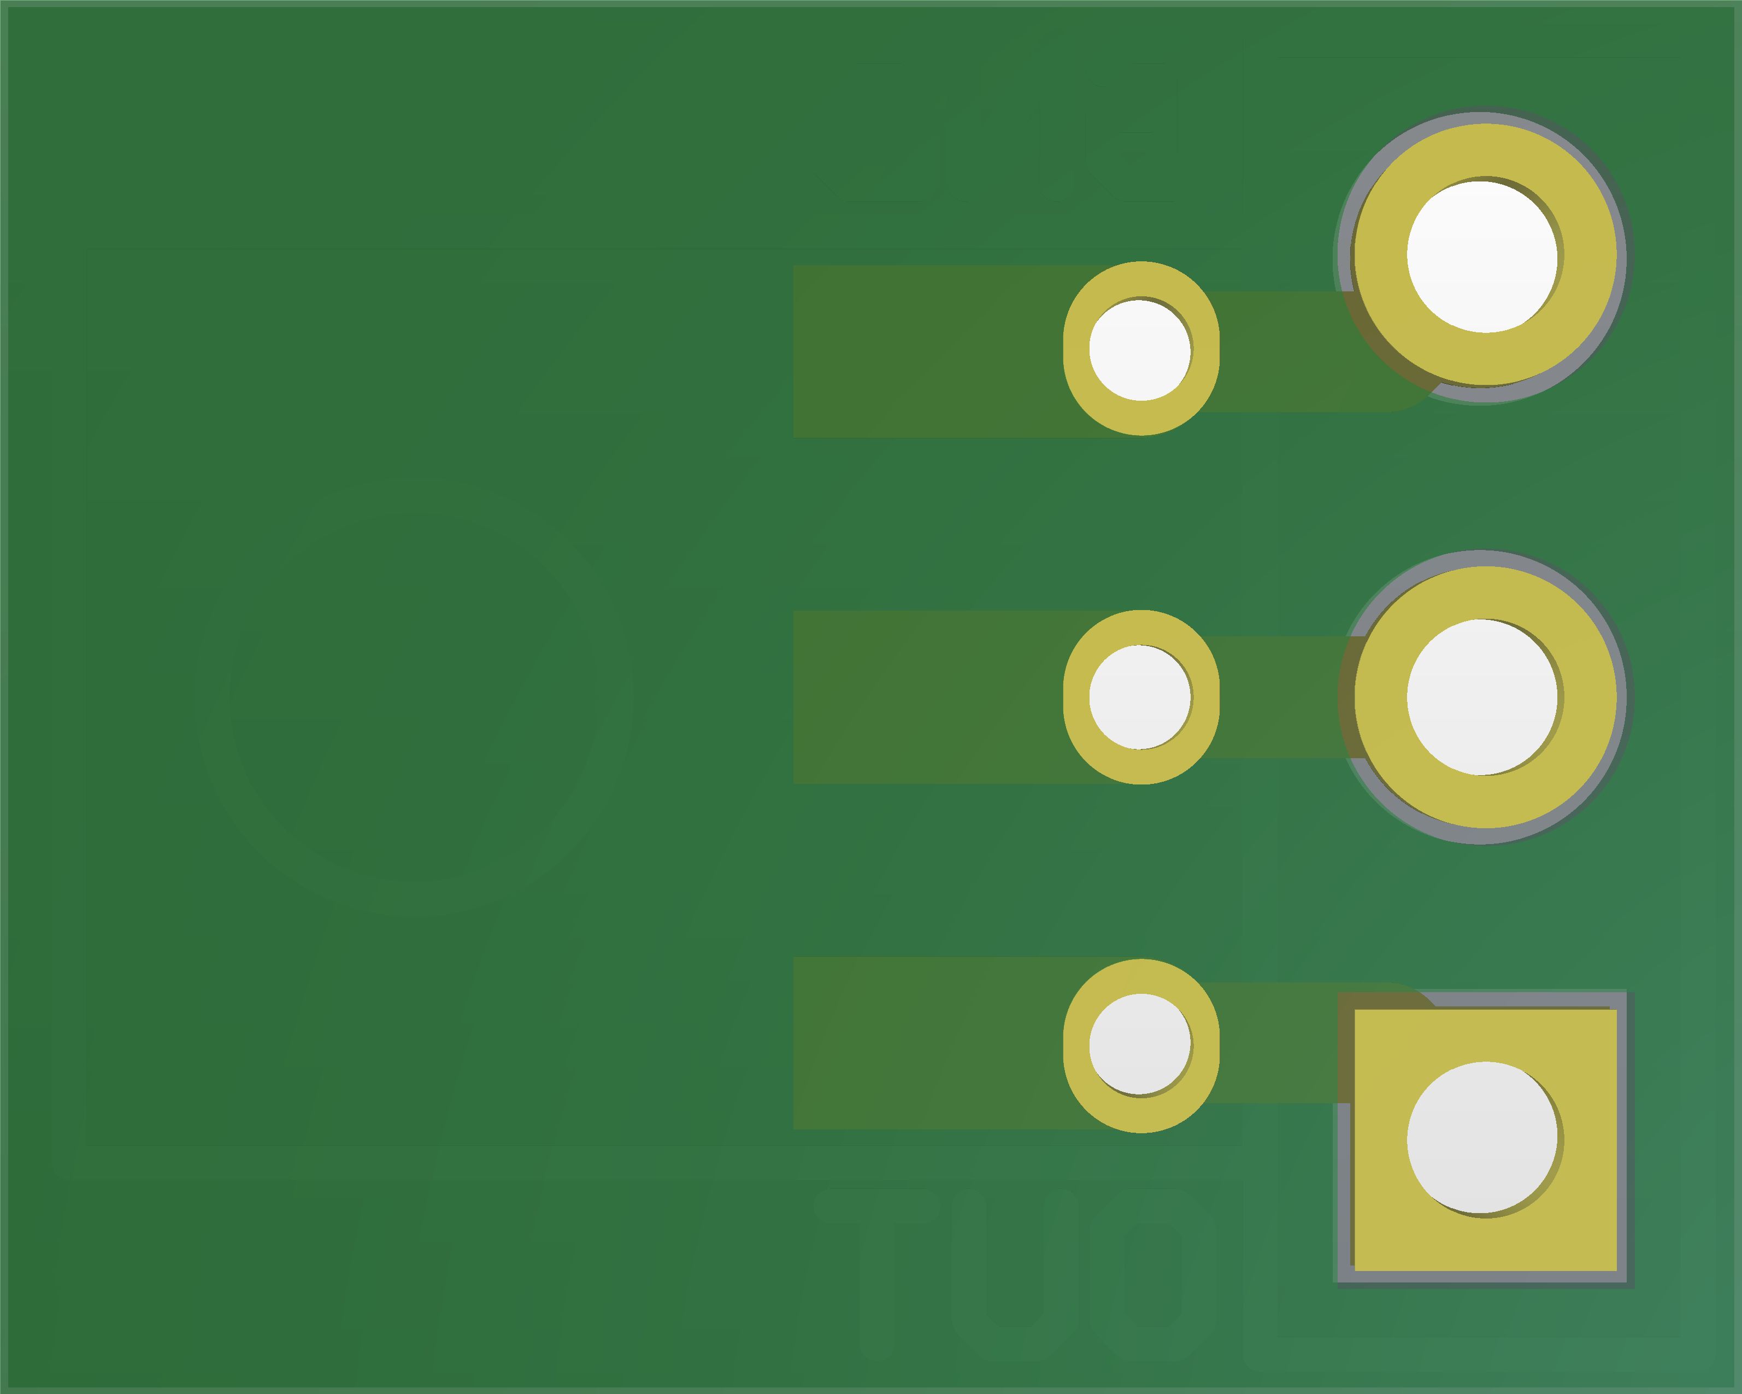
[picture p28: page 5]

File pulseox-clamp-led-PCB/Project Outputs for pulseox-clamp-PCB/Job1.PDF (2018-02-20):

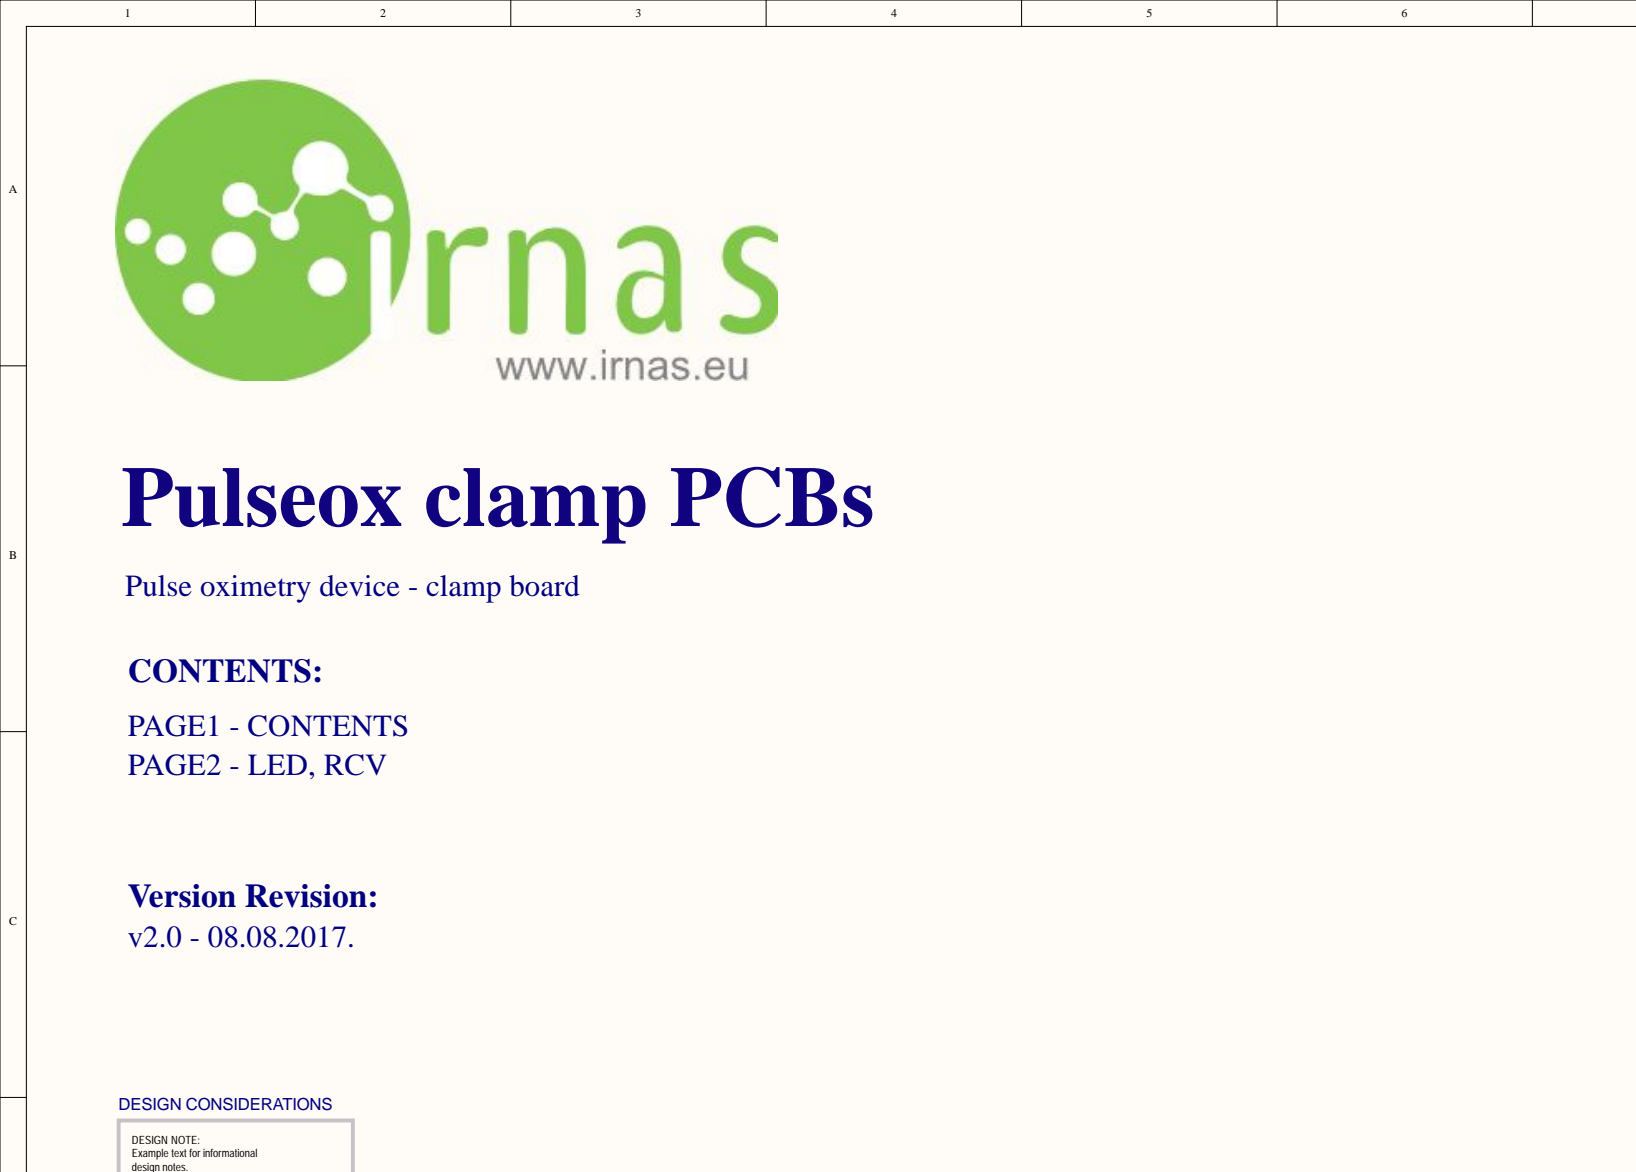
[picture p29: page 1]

Pulse oximetry device - clamp board

DESIGN NOTE:
Example text for informational
design notes.


LEDs and receiver schematics Transmitter board123



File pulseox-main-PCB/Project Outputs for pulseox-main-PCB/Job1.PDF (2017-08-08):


Pulse oximetry device - main board

DESIGN NOTE:
Example text for informational
design notes.

Example text for critical

pulseox-main-PCB.PrjPcb
PAGE1 - CONTENTS.SchDoc

LAYOUT NOTE:
layout guidelines.

Size: | DWG NO | Revision: v2.0

* Date: | 1 2 Sheet of


Power, MCU and Connectors schematics

LAYOUT NOTE:
All display capacitors
need to be close to
display connector.

DESIGN NOTE:
Two option for turning on display back light.
1. Hardware - button

pulseox-main-PCB.PrjPcb
PAGE2 - POWER, MCU.SchDoc

Size: | DWG NO | Revision: v2.0

* Date: | * * Sheet of









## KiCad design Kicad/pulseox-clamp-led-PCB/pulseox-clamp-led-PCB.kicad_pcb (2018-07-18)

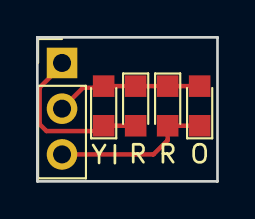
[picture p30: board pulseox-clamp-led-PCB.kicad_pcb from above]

Board: 2 copper layers, 10.0 x 8.0 mm, 5 parts (0 on the bottom side), 3 nets.

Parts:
I: LED; LED_0805
O: LED; LED_0805
P1: Header 3; Pin_Header_Straight_1x03_Pitch2.54mm
R: LED; LED_0805
Y: LED; LED_0805

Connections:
unnamed: I.2, P1.1, Y.1
unnamed: I.1, O.2, P1.2, R.1, Y.2
unnamed: O.1, P1.3, R.2

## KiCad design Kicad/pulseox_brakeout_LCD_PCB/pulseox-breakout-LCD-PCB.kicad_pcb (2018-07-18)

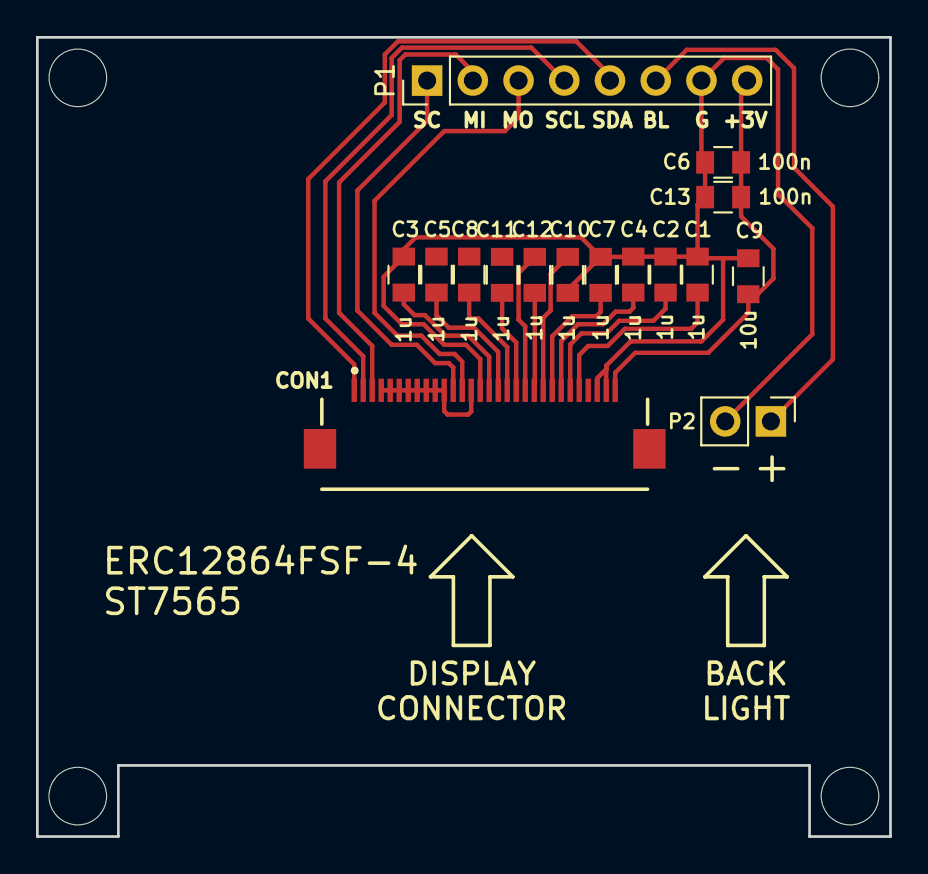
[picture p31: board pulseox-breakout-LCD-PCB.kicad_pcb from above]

Board: 2 copper layers, 47.4 x 44.4 mm, 20 parts (0 on the bottom side), 20 nets.

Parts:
C1, C2, C3, C4, C5, C7, C8, C10, C11, C12: 1u; C_0805
C6, C13: 100n; C_0805
C9: 10u; C_0805
CON1: P3; FH12-30S-0.5SH(55)
MK1, MK2, MK3, MK4: Mounting_Hole; MountingHole_3.2mm_M3
P1: Header 8; Pin_Header_Straight_1x08_Pitch2.54mm
P2: Header 2; Pin_Header_Straight_1x02_Pitch2.54mm

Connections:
+3V3: C6.2, C9.2, C13.2, CON1.4, CON1.5, CON1.6, CON1.7, CON1.8, CON1.9, CON1.10, CON1.11, CON1.14, CON1.30, P1.8
B_LIGHT: P1.6, P2.1
GND: C1.1, C2.1, C3.1, C4.1, C6.1, C7.1, C9.1, C10.1, C13.1, CON1.15, CON1.28, CON1.29, P1.7, P2.2
unnamed: C1.2, CON1.26
unnamed: C2.2, CON1.25
unnamed: C3.2, CON1.16
unnamed: C4.2, CON1.24
unnamed: C5.2, CON1.17
unnamed: C7.2, CON1.23
unnamed: C8.2, CON1.18
unnamed: C10.2, CON1.22
unnamed: C5.1, C8.1, C11.1
unnamed: C11.2, CON1.19
unnamed: C12.1, CON1.20
unnamed: C12.2, CON1.21
PA5/SCK: CON1.12, P1.1
PA6/MISO: CON1.3, P1.2
PA7/MOSI: CON1.13, P1.3
PA9/SCL: CON1.2, P1.4
PA10/SDA: CON1.1, P1.5

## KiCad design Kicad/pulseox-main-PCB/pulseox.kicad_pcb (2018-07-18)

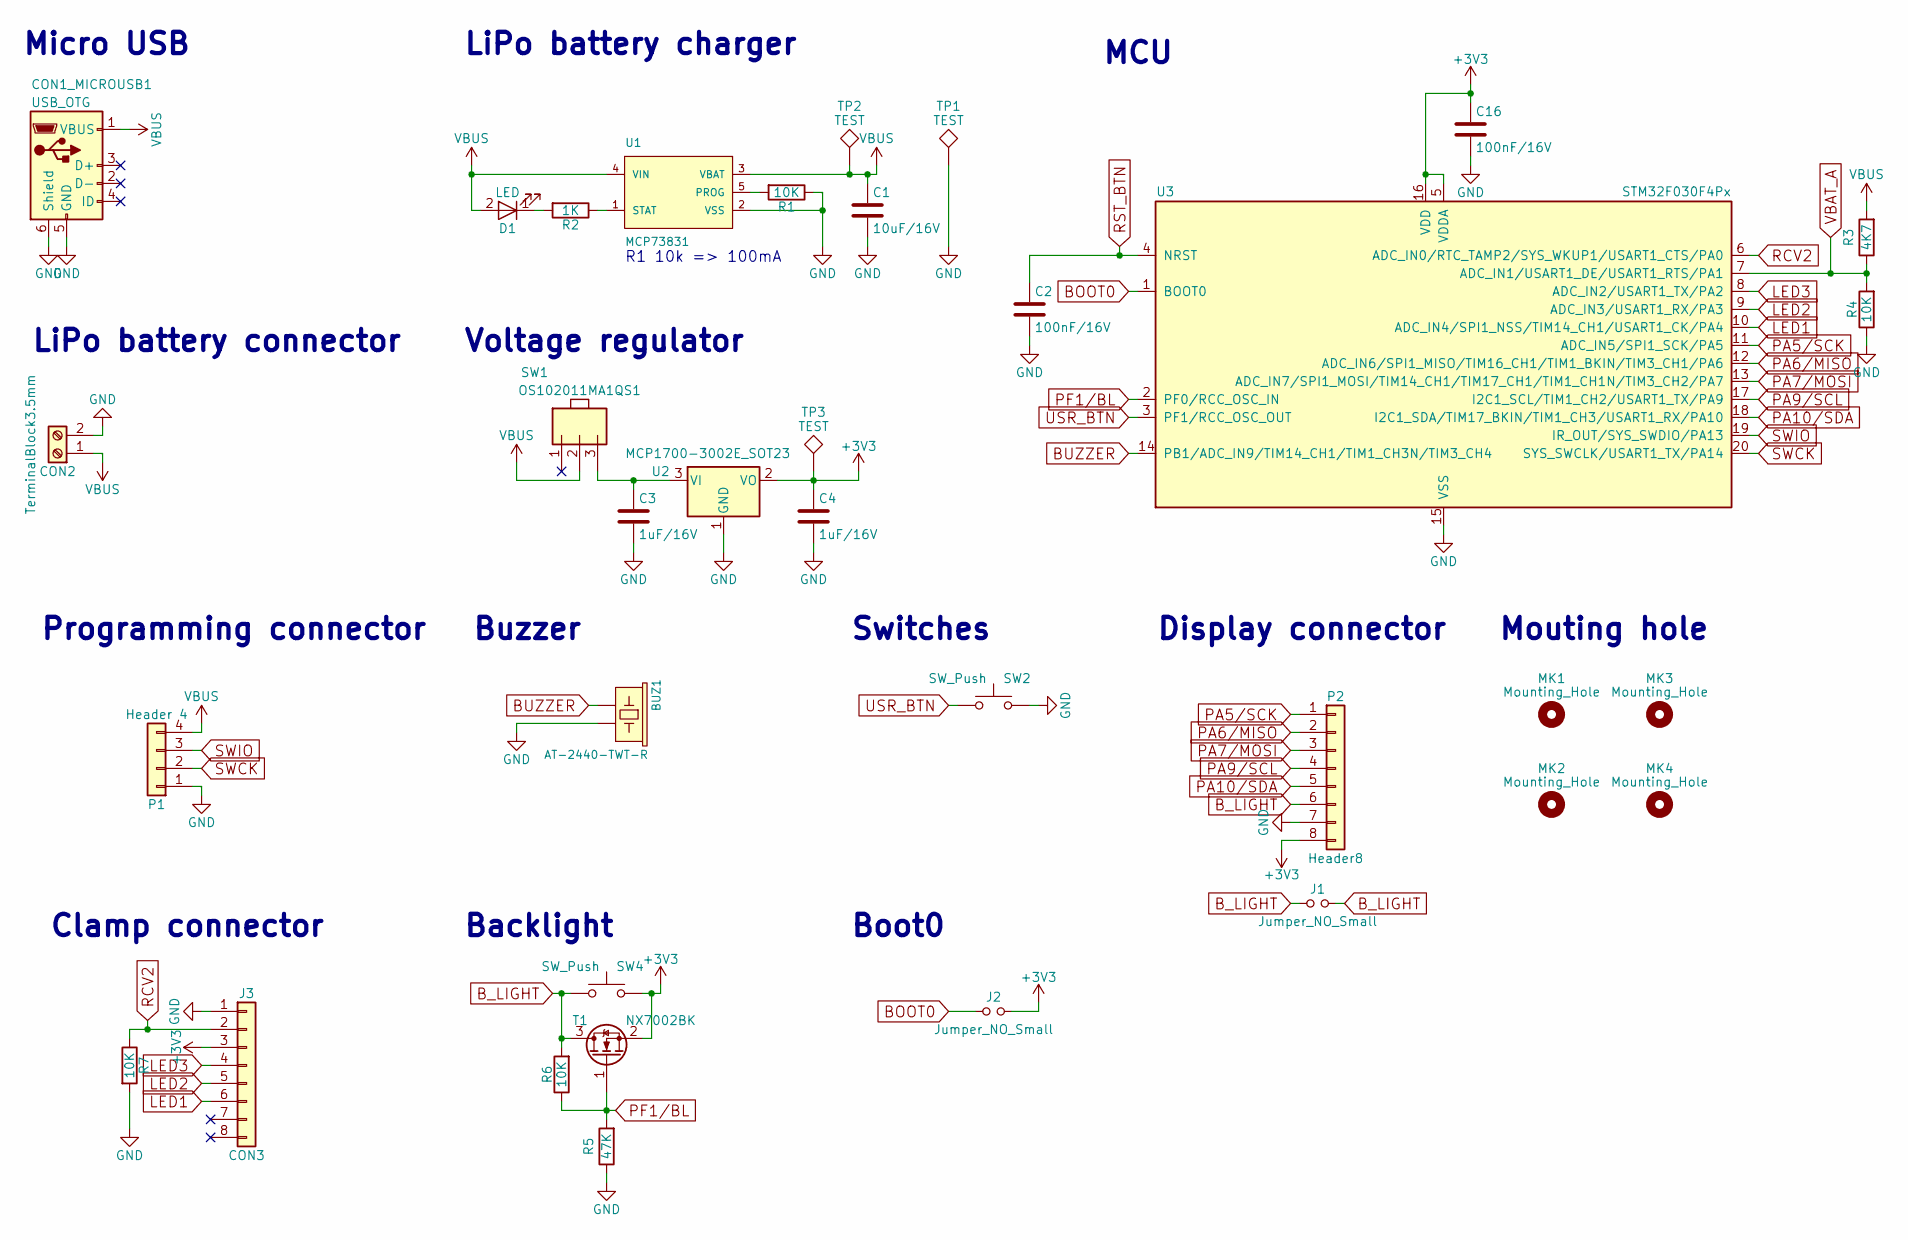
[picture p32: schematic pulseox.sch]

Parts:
BUZ1: AT-2440-TWT-R
C1: 10uF/16V; C_0805
C2, C16: 100nF/16V; C_0805
C3, C4: 1uF/16V; C_0805
CON1_MICROUSB1: USB_OTG; USB_Micro-B_Molex-105017-0001
CON2: TerminalBlock3.5mm; TerminalBlock_Phoenix_PT-3.5mm_2pol
D1: LED; LED_0603
J1: Jumper_NO_Small; R_0805
J2: Jumper_NO_Small; SMT-JUMPER_2_NO_SILK
J3: CON3; RJ45_8
MK1, MK2, MK3, MK4: Mounting_Hole; MountingHole_3.2mm_M3_ISO7380
P1: Header 4; Pin_Header_Straight_1x04_Pitch2.54mm
P2: Header8; Pin_Header_Straight_1x08_Pitch2.54mm
R1: 10K; R_0603
R2: 1K; R_0603
R3: 4K7; R_0805
R4, R6, R7: 10K; R_0805
R5: 47K; R_0805
SW1: OS102011MA1QS1
SW2, SW4: SW_Push; SWITCH TACTILE SPST-NO 0.05A 12V
T1: NX7002BK; SOT65P210X110-3N
TP1, TP2, TP3: TEST; Measurement_Point_Round-SMD-Pad_Small
U1: MCP73831; SOT23-5
U2: MCP1700-3002E_SOT23; SOT-23
U3: STM32F030F4Px; TSSOP-20_4.4x6.5mm_Pitch0.65mm

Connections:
+3V3: C4.1, C16.1, J2.2, J3.3, P2.8, SW4.2, T1.2 (S), TP3.1, U2.2 (VO), U3.5 (VDDA), U3.16 (VDD)
BOOT0: J2.1, U3.1 (BOOT0)
BUZZER: BUZ1.+ (1), U3.14 (PB1/ADC_IN9/TIM14_CH1/TIM1_CH3N/TIM3_CH4)
B_LIGHT: J1.1, J1.2, P2.6, R6.2, SW4.1, T1.3 (D)
GND: BUZ1.- (2), C1.2, C2.2, C3.2, C4.2, C16.2, CON1_MICROUSB1.5 (GND), CON1_MICROUSB1.6 (Shield), CON2.2, J3.1, P1.1, P2.7, R1.1, R4.1, R5.1, R7.2, SW2.2, TP1.1, U1.2 (VSS), U2.1 (GND), U3.15 (VSS)
LED1: J3.6, U3.10 (ADC_IN4/SPI1_NSS/TIM14_CH1/USART1_CK/PA4)
LED2: J3.5, U3.9 (ADC_IN3/USART1_RX/PA3)
LED3: J3.4, U3.8 (ADC_IN2/USART1_TX/PA2)
unnamed: C3.1, SW1.3, U2.3 (VI)
unnamed: D1.1 (K), R2.2
unnamed: R1.2, U1.5 (PROG)
unnamed: R2.1, U1.1 (STAT)
PA5/SCK: P2.1, U3.11 (ADC_IN5/SPI1_SCK/PA5)
PA6/MISO: P2.2, U3.12 (ADC_IN6/SPI1_MISO/TIM16_CH1/TIM1_BKIN/T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)
PA7/MOSI: P2.3, U3.13 (ADC_IN7/SPI1_MOSI/TIM14_CH1/TIM17_CH1/T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)
PA9/SCL: P2.4, U3.17 (I2C1_SCL/TIM1_CH2/USART1_TX/PA9)
PA10/SDA: P2.5, U3.18 (I2C1_SDA/TIM17_BKIN/TIM1_CH3/USART1_RX/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)
PF1/BL: R5.2, R6.1, T1.1 (G), U3.2 (PF0/RCC_OSC_IN)
RCV2: J3.2, R7.1, U3.6 (ADC_IN0/RTC_TAMP2/SYS_WKUP1/USART1_CTS/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)
RST_BTN: C2.1, U3.4 (NRST)
SWCK: P1.2, U3.20 (SYS_SWCLK/USART1_TX/PA14)
SWIO: P1.3, U3.19 (IR_OUT/SYS_SWDIO/PA13)
USR_BTN: SW2.1, U3.3 (PF1/RCC_OSC_OUT)
VBAT_A: R3.1, R4.2, U3.7 (ADC_IN1/USART1_DE/USART1_RTS/PA1)
VBUS: C1.1, CON1_MICROUSB1.1 (VBUS), CON2.1, D1.2 (A), P1.4, R3.2, SW1.2, TP2.1, U1.3 (VBAT), U1.4 (VIN)

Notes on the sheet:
R1 10k => 100mA
Micro USB
LiPo battery charger
LiPo battery connector
Voltage regulator
Programming connector
Buzzer
Clamp connector
Backlight
Switches
Boot0
MCU
Display connector
Mouting hole

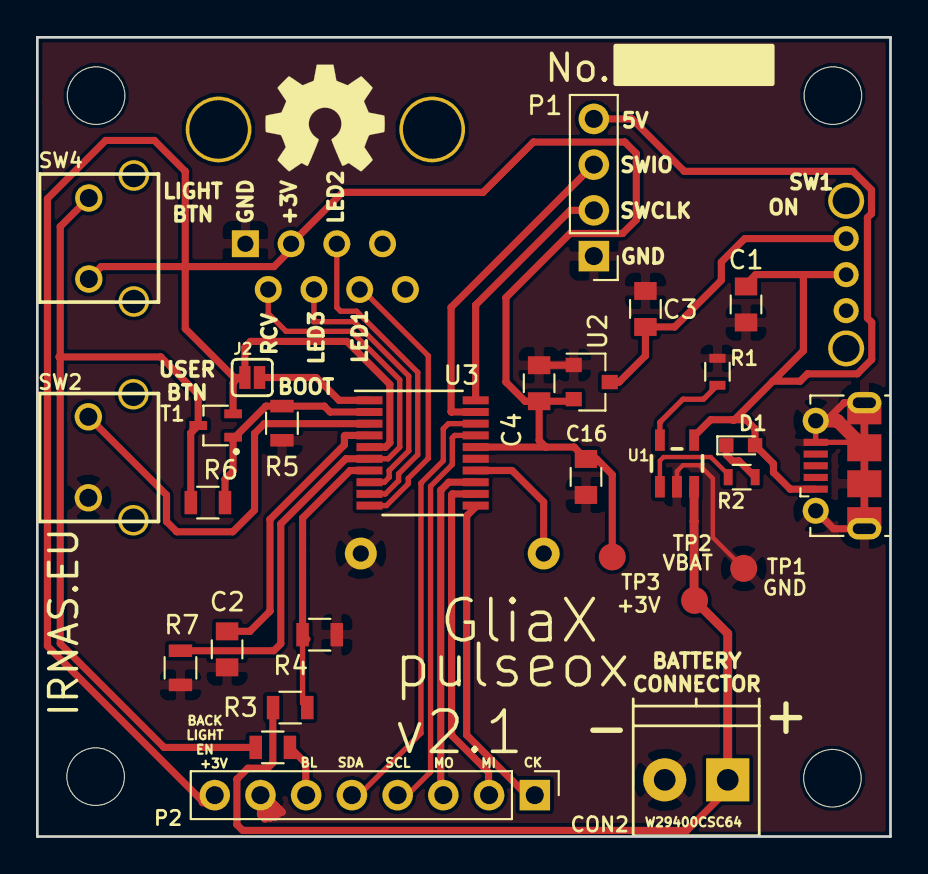
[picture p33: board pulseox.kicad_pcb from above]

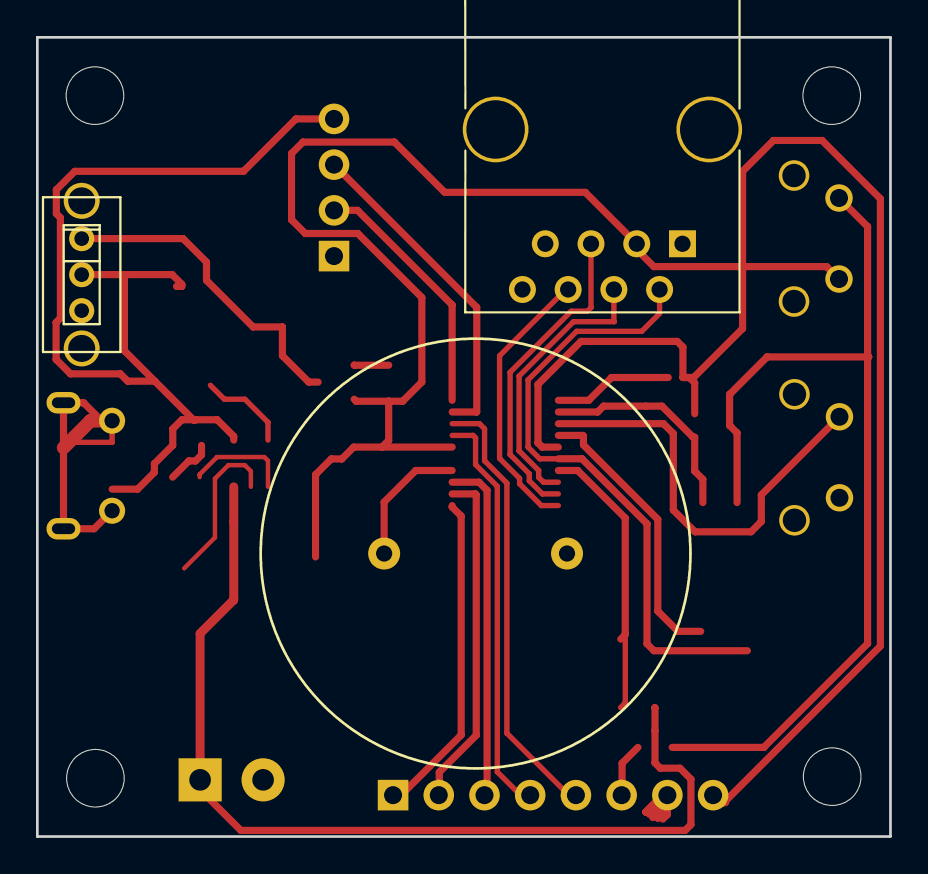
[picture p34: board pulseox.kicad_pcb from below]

Board: 2 copper layers, 47.4 x 44.4 mm, 35 parts (3 on the bottom side), 25 nets.

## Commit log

2017-04-18 Added Schematics
    [Pulseox.kicad_pcb, Pulseox.sch]
2017-04-19 Updated schematic
    [Pulseox.sch]
2017-07-19 git ignore main pcb
    [Pulseox.kicad_pcb]
2017-07-19 new project
    [PAGE1 - CONTENTS.SchDoc, PAGE2 - POWER, MCU.SchDoc, pulseox-main-PCB.PcbDoc, pulseox-main-PCB.PrjPcb]
2017-07-19 main pcb outline
    [pulseox-main-PCB.PcbDoc, pulseox-main-PCB.PrjPcb]
2017-07-20 sch done, need to be reviewed
    [PAGE2 - POWER, MCU.SchDoc, SHR-06V-S-B.STEP, SHR-06V-S.STEP, SM06B-SRSS-TB.STEP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]
2017-08-07 sch and pcb shape update
    [CK_Slide.step, PAGE2 - POWER, MCU.SchDoc, RES-0805.step, fsmsm.stp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]
2017-08-08 new version v2.0 done
    [JST_SM02B-SRSS-TB.step, PAGE2 - POWER, MCU.SchDoc, SOT-23.step, buzz.stp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]
2017-08-08 documentation update
    [PAGE1 - CONTENTS.SchDoc, pulseox-main-PCB.PcbDoc, pulseox-main-PCB.PrjPcb]
2017-08-08 clamp pcb project
    [PAGE1 - CONTENTS.SchDoc, PAGE2 - LED, RCV.SchDoc, pulseox-clamp-PCB.PrjPcb]
2017-08-09 clamp pcb update
    [PAGE2 - LED, RCV.SchDoc, pulseox-clamp-PCB-PCBLib.PcbLib, pulseox-clamp-PCB-SCHLib.SchLib, pulseox-clamp-PCB.PcbDoc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]
2017-08-10 pcb update v2.0 gerbers done
    [PAGE1 - CONTENTS.SchDoc, PAGE2 - LED, RCV.SchDoc, pulseox-clamp-PCB-PCBLib.PcbLib, pulseox-clamp-PCB-SCHLib.SchLib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]
2017-10-16 Update and rename Housing and Finger Clip/test_procedure/testing procedure.md to testing and debugging/01 firmware flashing instructions.md
2018-01-04 Rename Housing and Finger Clip/build_files/README.md to Housing and Finger Clip/housing/README.md
2018-01-04 Rename Housing and Finger Clip/build_files/case_bottom.STEP to Housing and Finger Clip/housing/case_bottom.STEP
    [case_bottom.STEP]
2018-01-04 Rename Housing and Finger Clip/housing/case_bottom.STEP to Housing and Finger Clip/housing/build_files/case_bottom.STEP
    [case_bottom.STEP]
2018-01-04 Rename Housing and Finger Clip/build_files_V2/README.md to Housing and Finger Clip/finger_clip/README.md
2018-02-20 new version of pulseox
    [Bill of Materials-pulseox-main-PCB.xlsx, Bill of Materials-pulseox-main-PCB_farnell_15_08_2017.xlsx, PAGE2 - LED, RCV.SchDoc, pcb_test.dxf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]
2018-07-16 v2.1 finished design
    [Bill of Materials-pulseox-main-PCB.xlsx, PAGE1 - CONTENTS.SchDoc, PAGE2 - POWER, MCU.SchDoc, User Library-SWITCH, TACTILE, RIGHT ANGLE, 12VDC, 50MA, 3_15MM ACT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]
2018-07-17 update docs
    [pulseox-clamp-PCB.PcbDoc, pulseox_brakeout_LCD_PCB.PcbDoc, pulseox_brakeout_LCD_PCB.PrjPcb]
2018-07-18 Added Kicad files
    [Bill of Materials-pulseox-main-PCB.xlsx, Pulseox.kicad_pcb, Pulseox.sch, pulseox-breakout-LCD-PCB.kicad_pcb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]
2018-07-18 Added output PDF files from Kicad project
    [pulseox-breakout-LCD-PCB.kicad_pcb, pulseox-breakout-LCD-PCB.sch, pulseox-clamp-PCB.kicad_pcb, pulseox-clamp-PCB.sch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]
